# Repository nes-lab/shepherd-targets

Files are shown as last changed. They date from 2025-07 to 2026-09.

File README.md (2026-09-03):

# Target Boards & Firmware





**Main Documentation**: <https://nes-lab.github.io/shepherd>

**Source Code**: <https://github.com/nes-lab/shepherd-targets>

**Main Project**: <https://github.com/nes-lab/shepherd>

---

The repository contains a collection of target-hardware and mcu-firmwares used by the shepherd-testbed.
In the past shepherd had a nRF52-only target but can now leverage an additional FRAM, as demonstrated successfully by the
[Riotee-Platform](https://www.riotee.nessie-circuits.de).

**NOTE**: The shepherd testbed has a second target-port (unused) and is looking for ideas.
Just contact us if you got ideas.

## nRF52 with MSP430FR as FRAM

The current hardware v1.3+ uses

- Nordic nRF52840 - primary MCU with RF
- TI MSP430FR5994 - secondary MCU with low-energy FRAM
- Abracon AB1805 - real-time clock

Target_nRF_MSP430

BOM, gerber-files and schematics are available in the [PCB-Directory](https://github.com/nes-lab/shepherd-targets/tree/main/hardware).
This folder also contains a guide for testing new target-PCBs.

Target_nRF_MSP430_render

### Features

- freedom to use both MCUs as needed (just as radio or FRAM) or disable when not needed (deep sleep)
- over-voltage protection for V_LV (max 3.9V)
- under-voltage protection with hysteresis for nRF
- one debug LEDs with separate supply for minimal impact on pwr-budget
- one self-powered LED to "burn" energy
- io pins not interfering with RF (nRF PS v1.6 page 578)
- LEDs / UART similar to [Riotee](https://www.riotee.nessie-circuits.de/)
- nRF uses low voltage mode (PSv1.1 page 61)
- 16x GPIO shared to host, current-limited with 240R star-configuration (every participant has that resistor on its port to also keep data rates >10 MHz)
- high & low power-good-signal (similar to Riotee)
- SMA-port for external antenna
- RF-Balun optimized for high output power (PS v1.8 ref circuit 7)
- ~~3rd possible way for reset (external)~~, beside jtag and pwr-cycle

### nRF52-Firmwares

- [nrf52_demo_rf](https://github.com/nes-lab/shepherd-targets/tree/main/firmware/nrf52_demo_rf): demo implementation for a simple node that sends BLE packets when energy budget allows it
- [nrf52_testable](https://github.com/nes-lab/shepherd-targets/tree/main/firmware/nrf52_testable): watches all gpio and reports with UART messages (verification after assembly)
  - ensures that pcb is assembled OK and both MCUs are programmable and show basic functions
  - what is not tested: watchdog, FRAM, RF-Frontend (-> use rf-demo or rf-survey), sleep power consumption
- [nrf52_rf_test](https://github.com/nes-lab/shepherd-targets/tree/main/firmware/nrf52_rf_test): sends out 1 BLE-Packet per second (verify with an app like `RaMBLE`)
- [nrf52_rf_survey](https://github.com/nes-lab/shepherd-targets/tree/main/firmware/nrf52_rf_survey): Link Matrix Generator - TX-Unit - sends packet with every possible P_TX, loops until stopped
- [nrf52_deep_sleep](https://github.com/nes-lab/shepherd-targets/tree/main/firmware/nrf52_deep_sleep): practically turned off MCU with the lowest possible consumption
- TODO: nrf52_spi_radio - default implementation to use nRF as a radio frontend

### MSP430FR-Firmwares

- [msp430_deep_sleep](https://github.com/nes-lab/shepherd-targets/tree/main/firmware/msp430_deep_sleep): practically turned off MCU with the lowest possible consumption
- [msp430_spi_fram](https://github.com/nes-lab/shepherd-targets/tree/main/firmware/msp430_spi_fram): [riotee](https://github.com/NessieCircuits/Riotee_MSP430Fram) implementation to use MSP as a flash storage
- [msp430_testable](https://github.com/nes-lab/shepherd-targets/tree/main/firmware/msp430_testable): switches on all shared gpio one by one (verification after assembly)

## Getting started

Step by step description for installing all prerequisites to compile the firmware.

### nRF52

- Make sure you have the [GNU Arm Embedded Toolchain](https://developer.arm.com/tools-and-software/open-source-software/developer-tools/gnu-toolchain/gnu-rm/downloads) installed
- If `arm-none-eabi-gcc` is not in your path, set the environment variable `GNU_INSTALL_ROOT` accordingly
  - e.g. `export GNU_INSTALL_ROOT=/opt/toolchain/` (note the trailing foreslash)
- Download the nRF5 SDK from [here.](https://www.nordicsemi.com/Software-and-tools/Software/nRF5-SDK/Download) (You don't need a SoftDevice) and extract it
- Set the environment variables `SDK_ROOT` to the corresponding absolute path, e.g.: `export SDK_ROOT=/home/user/nRF5_SDK_17.0.2_d674dde/`
- run `make`

Refer to [the GitHub workflow](https://github.com/nes-lab/shepherd-targets/tree/main/.github/workflows/build_nrf.yaml) for how to install the toolchain and build the project.

### MSP430

To build the code, you'll need the gcc toolchain for the MSP430 microcontroller series.
Refer to [the GitHub workflow](https://github.com/nes-lab/shepherd-targets/tree/main/.github/workflows/build_msp.yaml) for how to install the toolchain and build the project.

### Controlling the Node-ID

When an `elf`-firmware contains a ``SHEPHERD_NODE_ID``, the variable will be patched with the actual target-ID before running the experiment.
See the proposed [c-file](https://github.com/nes-lab/shepherd-targets/tree/main/firmware/nrf52_demo_rf/src/shepherd_node_id.c) for more information.

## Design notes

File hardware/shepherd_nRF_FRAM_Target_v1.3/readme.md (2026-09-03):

# nRF52 & MSP430 FRAM Target V1.3

Shared pins between MCUs and Observers with **Cape V2.5 (currently evaluated)**.
**The testbed still uses Cape v2.4 as of 2025-04. See 2nd table below for that mapping.**

| SHP-V26  | Dir   | Riotee     | nRF52  | msp430  | Description                 |
|----------|-------|------------|--------|---------|-----------------------------|
| GPIO0    | <-A-> | GPIO.0     | P0.21  | P2.6    | UART Target-RX, msp.A1.CiPo |
| GPIO1    | <--   | GPIO.1     | P0.08  | P2.5    | UART Target-TX, msp.A1.CoPi |
| GPIO2    | <-B-> | GPIO.2     | P0.04  | P2.3    | msp.A1.PSel                 |
| GPIO3    | <-B-> | GPIO.3     | P0.05  | P2.4    | msp.A1.CLK                  |
| GPIO4    | <-C-> | GPIO.4     | P1.09  | P4.6    |                             |
| GPIO5    | <-C-> | GPIO.5     | P0.26  | P3.6    |                             |
| GPIO6    | <-C-> | GPIO.6     | P1.03  | PJ.6    |                             |
| GPIO7    | <-C-> | GPIO.7     | P0.11  | P5.3    | msp.B1.PSel                 |
| GPIO8    | <--   | GPIO.8     | P0.13  | P5.2    | msp.B1.CLK                  |
| GPIO9    | <--   | GPIO.9     | P0.16  | P5.1    | msp.B1.CiPo                 |
| GPIO10   | <--   | -          | P0.12  | P5.0    | msp.B1.CoPi, SDA            |
| GPIO11   | <--   | -          | P0.10  | P6.0    | msp.A3.CoPi, TXD            |
| (GPIO12) | <--   | -          | P0.19  | P6.1    | msp.A3.CiPo, RXD            |
| (GPIO13) | <--   | -          | P0.20  | P6.3    | msp.A3.STE                  |
| (GPIO14) | <--   | -          | P0.24  | P6.6    | msp.A3.CLK                  |
| (GPIO15) | <--   | -          | P0.27  | P6.7    | msp.A3.STE                  |
| PwrGoodL | -->   | PG_L       | P0.23  | P5.4    |                             |
| PwrGoodH | -->   | PG_H       | P0.07  | P5.5    |                             |
| prog11   | -->   | SWD.CLK    | swdclk | -       |                             |
| prog12   | <-D-> | SWD.IO     | swdio  | -       |                             |
| prog21   | -->   | SBW.CLK    | -      | sbwtck  |                             |
| prog22   | <-E-> | SBW.IO     | -      | sbwtdio |                             |
|          | -     | LED.0      | P1.13  | P5.7    |                             |
|          | -     | LED.2P     | P0.03  | PJ.0    |                             |
|          | -     | I2C.SCL    | P1.08  | P6.5    |                             |
|          | -     | I2C.SDA    | P0.06  | P6.4    |                             |
|          | -     | RTC.INT    | P0.30  | P7.3    | shared, no fct for shp      |
|          | -     | MAX.INT    | P0.25  | PJ.1    | shared, no fct for shp      |
|          | -     | C2C.CLK    | P0.18  | P1.5    | msp.A0.CLK                  |
|          | -     | C2C.CoPi   | P0.17  | P2.0    | msp.A0.CoPi                 |
|          | -     | C2C.CiPo   | P0.14  | P2.1    | msp.A0.CiPo                 |
|          | -     | C2C.PSel   | P0.22  | P1.4    | msp.A0.PSel                 |
|          |       | C2C.GPIO   | P0.15  | PJ.2    |                             |
|          |       | THRCTRL.H0 | P0.09  | P1.3    | shared, no fct for shp      |
|          |       | THRCTRL.H1 | P1.02  | P3.3    | shared, no fct for shp      |
|          |       | THRCTRL.L0 | P1.07  | P6.2    | shared, no fct for shp      |
|          |       | THRCTRL.L1 | P1.04  | P7.0    | shared, no fct for shp      |
|          |       | VCAP.Sense | P0.29  | P7.5    | VTarget                     |

**Note**:

- A, B, C in DIR-Column refer to switch-groups. 1, 2 and/or 4 bits can be reversed to talk to the target.
- D, E are switch-groups needed for programming
- Shepherds GPIO12 to GPIO15 are not recordable by the testbed as pins on the SBC are all used up

## Connections to Cape V2.4 via Adapter

The 40-pin Edge-Connector of Target V1.3 has an adapter to interface the 2x9 Header of Cape V2.4. This keeps connections compatible to Target V1.0.

| SHP-V24 | Dir   | Riotee   | nRF52  | msp430  | Description                 |
|---------|-------|----------|--------|---------|-----------------------------|
| GPIO0   | <-A-> | GPIO.7   | P0.11  | P5.3    | msp.B1.PSel                 |
| GPIO1   | <-A-> | GPIO.8   | P0.13  | P5.2    | msp.B1.CLK                  |
| GPIO2   | <-A-> | GPIO.2   | P0.04  | P2.3    | msp.A1.PSel                 |
| GPIO3   | <-A-> | GPIO.3   | P0.05  | P2.4    | msp.A1.CLK                  |
| GPIO4   | <--   | GPIO.4   | P1.09  | P4.6    |                             |
| GPIO5   | <--   | GPIO.5   | P0.26  | P3.6    |                             |
| GPIO6   | <--   | GPIO.6   | P1.03  | PJ.6    |                             |
| GPIO7   | <--   | GPIO.1   | P0.08  | P2.5    | UART Target-TX, msp.A1.CoPi |
| GPIO8   | <-B-> | GPIO.0   | P0.21  | P2.6    | UART Target-RX, msp.A1.CiPo |
| BATOK   | -->   | PG_H     | P0.07  | P5.5    |                             |
| prog11  | -->   | SWD.CLK  | swdclk | -       |                             |
| prog12  | <-C-> | SWD.IO   | swdio  | -       |                             |
| prog21  | -->   | SBW.CLK  | -      | sbwtck  |                             |
| prog22  | <-D-> | SBW.IO   | -      | sbwtdio |                             |

**Note**:

- A, B, C, D in DIR-Column refer to switch-groups
- Shepherds GPIO8 (target-rx) will be re-assigned to PwrGoodL (BATOK is PwrGoodH)
  - TODO: Resistor-Switch on adapter available, but software not ready yet

## Features

- similarity to Riotee
- MCU 1 - nRF52840
- MCU 2 - msp430FR5994
- low power RTC & Watchdog
- one led to burn energy fast
- SMA port to connect external antenna
  - balun is optimized for higher transmit power (>= 5 dBm, ref circuit 7 in PS v1.8)
- MCUs share SPI-Connection + some additional pins
- edge-connector routes out
  - programming pins (SWD & SBW)
  - power-good signals
  - 16x shared GPIO
- all shared GPIO is current limited to prevent damages to the hardware
  - limit to 8-10 mA @ 4V with 470 R or (2x) 220 R on each IC entry
- IO-Pins not interfering with RF (nRF PS v1.6 page 578)
- clock-crystals have high precision, 5 ppm, with matched impedance
- protection for over- & under-voltage, see sub-chapters below

### Over-Voltage-Protection

The target voltage coming from the shepherd-cape can reach up to 5 V.
The MCUs on the target board can't handle that voltage, so the ICs have to be protected.

Abs Max Ratings:

- 3.9 V nRF52
- 3.8 V RTC AB1805
- 4.1 V MSP430

A fitting shottky diode is used to burn energy above 3.7V.

One PMEG10010ELR Diode is between V_target and 3V3:

- 0.0 V -> 6 pA (noise)
- 0.1 V -> 47 nA
- 0.2 V -> 2.3 uA
- 0.3 V -> 120 uA
- 0.4 V -> 4.83 mA

### Under-Voltage-Protection

- the nRF consumes ~.5mA below 1.7V, even in deep-sleep
- consumption drops when going above 1.69 V
- consumption rises when going below 1.58 V
- tested 13 nodes range from
  - ON = 1.63 to 1.69 V
  - OFF = 1.58 to 1.60 V

Solution

- analog switch controlled by comparator with small hysteresis
- VON = 1.729 V, VOFF = 1.652 V according to formular in datasheet (values are wrong?)
- VON = 1.797 V, VOFF = 1.642 V when solving the network with traditional methods
- VON = 1.802 V, VOFF = 1.641 V from actual measurements

Possible Caveats

- hysteresis is currently only 150 mV and unstable behavior must be avoided
- charging the decoupling caps (2.6 uF) of the MCUs leads to voltage drop
  - 10 uF storage, 2.6 uF decoupling -> 230 mV drop (trouble)
  - 47 uF storage, 2.6 uF decoupling -> 48 mV drop
  - 100 uF storage, 2.6 uF decoupling -> 22 mV drop
- turning on the switch shows current spike of ~ 4 mA for < 50 us for target v1.0 with 1.6 uF decoupling
  - 10 uF storage, 5 mA draw -> 200 us for 100 mV drop
  - 10 uF storage, 1 mA draw -> 1000 us for 100 mV drop
  - 47 uF storage, 5 mA draw -> 940 us for 100 mV drop
  - 100 uF storage, 5 mA draw -> 2000 us for 100 mV drop

Calculating the charging drop for the decoupling caps with `maxima`:

```maxima
C_store: 10e-6;
C_out: 2.6e-6;
V_set: 1.7;
dVc: V_set * (sqrt(1 - C_out / C_store) - 1);
```

Calculating the allowed time for high current during switching on:

```maxima
V_set: 1.7;
C_store: 10e-6;
I_out: 5e-3;
dV: 100e-3;
t: dV * C_store / I_out;
```

See `.wxmx`-maxima-file for more details.

## Difference to Riotee

- nRF52840 instead of Riotees -833
  - main makefile specifies `NRF_DEV_NUM`
- msp430FR5994 has more storage (256 KB)
  - Size of FRAM auto-adjust? -> main makefile `RIOTEE_RAM_RETAINED_SIZE`, `RIOTEE_STACK_SIZE`
- extra LED.0
- 16x GPIO instead of 10x
- no power-converters, but over-voltage-protection and under-volt-switch for nRF

## Bugs of prior Version & Proposed Fixes / Improvements

- nRF - remove resist of alignment crosses
- less paste on thermal pad of nRF? Thermal paste is OK
  - solder on thermal is 9 * 1.1² = 8.6 mm² (round) -> 38 %
  - info: nRF-IC thermal pad ~4.75², 22.6 m² (IC and footprint match)
- make ABx Thermal pad bigger
  - info: ABx-IC thermal pad is ~ (1.8 mm)²
  - datasheet says D2xE2 is 1.65 - 1.75 - 1.85 -> area: 2.6 - 3.1 - 3.4 mm²
  - footprint was (1.13mm)² with 50% paste reduction (1.27 / 0.65 mm²)
  - now it is 1.5² with 65% reduction (2.25 / 0.79 mm²)
- stencil holes of nRF a bit bigger - pad 0.26mm round = 53.1e-3 mm², now with .28mm stencil (.213 distance, 61.6e-3 mm²)
  - ref design: pads .275mm with 19% expansion (.012mm) -> measured .299 (area .0594, .0647, .0702 for .275, .287, .299)
- stencil holes of MSP a bit bigger - pad 0.25mm round = 49.1e-3 mm², now with .28mm stencil (.213 distance)
- 1uF has two versions in BOM -> 10V version stays
- make more clear what is DNP -> Variants "Only Populate" changes Value, Mnf PN, Price to DNP
- Riotee has an MSP430FR5962 (like target v1.0) and not the current 5994?!? (256 vs 128 kByte)
  - linker and makefile needed a small adaption (include proper device-file)
  - Riotees FRAM-firmware is adapting automatically to FRAM-Size
  - datasheets memory map (section 9.15) shows identical maps with just double the FRAM-Space (end at x43FFF instead of x23FFF)
- why did the crystals footprint change (larger) but not the part? tombstone rate ~ 50%
  - correct crystal for that larger footprint: 520-ECX-.327CDX-1293, 5ppm, 3.2x1.5mm -> all correct & available
  - OLD: CM8V-T1A-32.768kHz-9pF-20PPM-TA-QC, 20ppm, 2.0x1.2mm
- add C on ABx-Crystal? YES - datasheet is misleading by not showing any
- board dimensions:
  - capes 54.8 / 2 = 27.4 mm max width -> 27
  - edge-connector, slit-bit is 6 x 17.4 mm -> side cutout is 6 x 4.8
  - target with hdr is 38.2 mm, so limiting the whole length now to 37
  - old-area was 25 x 24 = 600 mm², new usable area is 27 x 31 = 837
- nRF has high current draw between 500...1650 mV -> VSrc with diode+cap is problematic
  - voltage sweep is plotted in [this graphic](emu_ramp.plot_0s000_to_40s000.png) and other
  - add comparator to delay power of nRF
  - fix targets: comparator + pwr-switch -> on when above 1.65 .. 1.70 V
    - off again when going below 1.4 V
  - 2x 6.5 MOhm Divider to
  - ~~TS5A23166DCUR~~ -> needs comparator
  - ~~in our stock: NLAS4684, FSA2258~~
  - 595-TS5A3167DCKR, ROn .9 Ohm, SC70-5, 50nA supply, SPST -> V_analog_max = VCC, V_EN_max = VIn_max = 6.5V
    - COM connected to NC (normally closed) when logic is LOW, so input is nEN!
  - 579-MCP6546RT-IOT, comparator, VIN+ gets Ref ResistorNW, When VIN- is below VIN+ the output is high (WANTED)
    - open drain output, so PU to 3V3 - switch has <20nA leakage, so ~100k should be fine
- extend to 16 GPIO
  - order adapter to old shepherd 2x9
  - order pinheader and sockets for the new port
  - which pins to add?
  - 2x10 Angled Socket: SQT-110-01-F-D-RA -> new 2x13: SQT-113-01-F-D-RA -> without Angle: SQT-113-01-F-D
  - 2x10 PinHeader: 2PH2-20-UA -> new 2x13 only available from samtec, but they fit next to each other -> 2PH2-16-UA + 2PH2-10-UA
  - width: 20.35/10*13=26.5mm or better 20.35/11*14=25.9mm, MAX of Cape is 54.7/2=27.35mm
  - PCB-Edge-Connectors: <https://www.mouser.de/c/connectors/card-edge-connectors/?number%20of%20positions=26%20Position%7C~30%20Position&instock=y&active=y&sort=pricing>
    - PCIe 1x is cheap, has 1 mm distance and comes as TH & SMD, but it is designed for thick PCBs
    - HSEC8-120-01-S-DV-A-GR-K: 40Con, Guide Rails 7x20.6mm 11.75mm high
    - HSEC8-120-01-S-DV-A-K: without guide rails only 7.8mm high
    - **HSEC8-120-01-L-DV-A-K-TR**: same, but cheaper
  - ~~FFC/FPC-Con~~: <https://www.mouser.de/c/connectors/ffc-fpc/ffc-fpc-connectors/?number%20of%20positions=26%20Position%7C~28%20Position%7C~30%20Position%7C~32%20Position&instock=y&active=y>
  - ~~FFC/FPC-Cable~~: <https://www.mouser.de/c/connectors/ffc-fpc/ffc-fpc-jumper-cables/?number%20of%20conductors=26%20Conductor%7C~28%20Conductor%7C~30%20Conductor%7C~32%20Conductor&instock=y&active=y>
- current-limit LED0 (MSP430 is lower prio, so it gets 470R)
- **NEW GPIO**
  - GP10 P0.12  P5.0 (UCB1SIMO/SDA)
  - GP11 P0.10  P6.0 (UCA3SIMO/TXD)
  - GP12 P0.19  P6.1 (UCA3SOMI/RXD)
  - GP13 P0.20  P6.3 (UCA3STE)
  - GP14 P0.24  P6.6 (UCA3CLK)
  - GP15 P0.27  P6.7 (UCA3STE)
  - LED0 P1.13  P5.7
- verify RF-Path
  - PS_v1.8 ref circuit 7 shows improved 4 component filter: 1pF, 4.7nH, 1.2pF, 2.2nH (NP0 5%, hf ind. 5%)
  - keepout under antenna-path for
  - fanout shorter and thinner, C1 directly on RFOUT and GND
- review problematic pins
- also disable MSP with switch (avoids cross-feeding via gpio)

## Cost of Production

- PCB-Fabrication
  - 190 € / 30 n with shipping
  - 1.6mm thick, 4 layer, .3mm vias - filled and capped, .1 mm traces and distance
  - electro-polished stencil
- BOM cost
  - parts for 1 n when ordering 10 n = 20.60 €
  - parts for n=10 are 182 € (18.20 €/n)
  - parts for n=20 are 360 € (18 €/n)
- Pick & place
  - 29 different parts, 120 in total
  - 0.5 mm pitch

### Ordering of Parts

- new C27 1pF: 100x 81-GJM1555C1H1R0JB1D
- new C28 1.2pF: 100x 81-GJM1555C1H1R2JB1D
- new L2 2.2nH: 100x 81-LQG15HZ2N2C02D
- ~~SMA-Con?~~
- new HSEC8-120-01-L-DV-A-K-TR: 20x 200-HSEC812001LDVAKT
  - new headers for old cape?
- more 1uF - 4x30 - 200x 81-GCM155C71A105KE8D
- more 12pF -8x30 - 250x 77-VJ0402A120JXQPBC
- 12x 240R per unit (more IO)
- switch + comparator (MCP6546, TS5A3167)
  - 3x 100k, 1x 10k, 1x 1M,
  - 2x 100nF
- 1x 470R

### Extra remark

- DNP: C20, SMA-Con, Antenna

## Verifying the PCBs

- first do a visual inspection
- front side has one cap DNP: C20, lower left corner, near edge-connector

### Assembly

- solder the SMA-Connector, add Antenna

### First Powerup

- 2 mA @ 3V on V_target without programming
- 0 mA @ 3V on 3V-Input

### Software-Prereqs

**NOTE**: all further tests are done on BBone

```Shell
cd ~
git clone https://github.com/nes-lab/shepherd-tools
cd shepherd-tools
git checkout dev
git pull

python3 ./extra/gen_firmwares.py
sudo python3 ./extra/gen_experiments.py
```

Put Target on BBone with Target on Port 1!

### Test all GPIO & LEDs

First test all used gpio with this fw-combo (msp toggles, nrf watches and reports via uart):

```Shell
sudo shepherd-sheep program -p A -m 1 -v 3 -t nrf52 /var/shepherd/content/fw/nes_lab/nrf52_testable/build.hex
sudo shepherd-sheep program -p A -m 2 -v 3 -t msp430 /var/shepherd/content/fw/nes_lab/msp430_testable/build.hex
sudo shepherd-sheep target-power -p A -v 3 --on
# new
sudo shepherd-sheep run /etc/shepherd/target_device_test1.yaml
```

NOTE: best done with inter-connector that only routes: pwr1, serial, programming-pins, pwr2
Check UART output with logic analyzer or in shepherd recording.
Behavior is described in [the firmware-directory](https://github.com/nes-lab/shepherd-targets/tree/main/firmware/nrf52_testable).

### Testing the Radio

```Shell
sudo shepherd-sheep program -p A -m 1 -v 3 -t nrf52 /var/shepherd/content/fw/nes_lab/nrf52_rf_test/build.hex
sudo shepherd-sheep program -p A -m 2 -v 3 -t msp430 /var/shepherd/content/fw/nes_lab/msp430_deep_sleep/build.hex
sudo shepherd-sheep target-power -p A -v 3 --on
# new
sudo shepherd-sheep run /etc/shepherd/target_device_test2.yaml
```

Behavior is described in [the firmware-directory](https://github.com/nes-lab/shepherd-targets/tree/main/firmware/nrf52_rf_test).

### Testing Power-consumption during sleep

```Shell
sudo shepherd-sheep program -p A -m 1 -v 3 -t nrf52 /var/shepherd/content/fw/nes_lab/nrf52_deep_sleep/build.hex
sudo shepherd-sheep program -p A -m 2 -v 3 -t msp430 /var/shepherd/content/fw/nes_lab/msp430_deep_sleep/build.hex
# new
sudo shepherd-sheep run /etc/shepherd/target_device_test3.yaml
```

## Testing

- programming via debug-adapter fails for nRF (OK for MSP), even at 200kbit or 100kbit instead of 500k
  - reason: unsoldered press-fit to shepherd cape
- 6 of 24 targets had trouble programming the MSP
  - removing two ICs showed no flaws
  - as visual inspection is OK the next suspects are: pcb or chip-failure
- report is in [planning-repo](https://github.com/orgua/shepherd-v2-planning/tree/main/doc_testbed)

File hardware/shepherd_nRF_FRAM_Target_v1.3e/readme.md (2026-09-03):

# nRF52 & MSP430 FRAM Target V1.3e

Shared pins between MCUs and Observers with **Cape V2.5 (deployed in near future / mid 2025)**.

~~The testbed still uses Cape v2.4 as of 2025-04. See 2nd table below for that mapping.~~

**Note**:

- GPIO12 to GPIO15 are not recordable by the testbed with cape V2.5, as pins on the SBC are all used up
- The nRF has no outer reset line
  - configuring one could keep the MCU in permanent reset
  - Code for the nRF52-DK may use P0.21 for reset - it is actively used for UART-Rx here.
- A, B, C in DIR-Column refer to switch-groups. 1, 2 and/or 4 bits can be reversed to talk to the target.
- D, E are switch-groups needed for programming

| Tgt-Port | Dir   | Riotee     | nRF52  | msp430  | Description                 |
|----------|-------|------------|--------|---------|-----------------------------|
| GPIO0    | <-A-> | GPIO.0     | P0.21  | P2.6    | UART Target-RX, msp.A1.CiPo |
| GPIO1    | <--   | GPIO.1     | P0.08  | P2.5    | UART Target-TX, msp.A1.CoPi |
| GPIO2    | <-B-> | GPIO.2     | P0.04  | P2.3    | msp.A1.PSel                 |
| GPIO3    | <-B-> | GPIO.3     | P0.05  | P2.4    | msp.A1.CLK                  |
| GPIO4    | <-C-> | GPIO.4     | P1.09  | P4.6    |                             |
| GPIO5    | <-C-> | GPIO.5     | P0.26  | P3.6    |                             |
| GPIO6    | <-C-> | GPIO.6     | P1.03  | PJ.6    |                             |
| GPIO7    | <-C-> | GPIO.7     | P0.11  | P5.3    | msp.B1.PSel                 |
| GPIO8    | <--   | GPIO.8     | P0.13  | P5.2    | msp.B1.CLK                  |
| GPIO9    | <--   | GPIO.9     | P0.16  | P5.1    | msp.B1.CiPo                 |
| GPIO10   | <--   | -          | P0.12  | P5.0    | msp.B1.CoPi, SDA            |
| GPIO11   | <--   | -          | P0.10  | P6.0    | msp.A3.CoPi, TXD            |
| (GPIO12) | <--   | -          | P0.19  | P6.1    | msp.A3.CiPo, RXD            |
| (GPIO13) | <--   | -          | P0.20  | P6.3    | msp.A3.STE                  |
| (GPIO14) | <--   | -          | P0.24  | P6.6    | msp.A3.CLK                  |
| (GPIO15) | <--   | -          | P0.27  | P6.7    | msp.A3.STE                  |
| PwrGoodL | -->   | PG_L       | P0.23  | P5.4    |                             |
| PwrGoodH | -->   | PG_H       | P0.07  | P5.5    |                             |
| prog11   | -->   | SWD.CLK    | swdclk | -       |                             |
| prog12   | <-D-> | SWD.IO     | swdio  | -       |                             |
| prog21   | -->   | SBW.CLK    | -      | sbwtck  |                             |
| prog22   | <-E-> | SBW.IO     | -      | sbwtdio |                             |
|          | -     | LED.0      | P1.13  | P5.7    |                             |
|          | -     | LED.2P     | P0.03  | PJ.0    |                             |
|          | -     | I2C.SCL    | P1.08  | P6.5    |                             |
|          | -     | I2C.SDA    | P0.06  | P6.4    |                             |
|          | -     | RTC.INT    | P0.30  | P7.3    | shared, no fct for shp      |
|          | -     | MAX.INT    | P0.25  | PJ.1    | shared, no fct for shp      |
|          | -     | C2C.CLK    | P0.18  | P1.5    | msp.A0.CLK                  |
|          | -     | C2C.CoPi   | P0.17  | P2.0    | msp.A0.CoPi                 |
|          | -     | C2C.CiPo   | P0.14  | P2.1    | msp.A0.CiPo                 |
|          | -     | C2C.PSel   | P0.22  | P1.4    | msp.A0.PSel                 |
|          |       | C2C.GPIO   | P0.15  | PJ.2    |                             |
|          |       | THRCTRL.H0 | P0.09  | P1.3    | shared, no fct for shp      |
|          |       | THRCTRL.H1 | P1.02  | P3.3    | shared, no fct for shp      |
|          |       | THRCTRL.L0 | P1.07  | P6.2    | shared, no fct for shp      |
|          |       | THRCTRL.L1 | P1.04  | P7.0    | shared, no fct for shp      |
|          |       | VCAP.Sense | P0.29  | P7.5    | VTarget                     |

## Connections to Cape V2.4 via Adapter

The 40-pin Edge-Connector of Target V1.3 has an adapter to interface the 2x9 Header of Cape V2.4.
This keeps connections compatible to Target V1.0.

**Note**:

- A, B, C, D in DIR-Column refer to switch-groups
- Shepherds GPIO8 (target-rx) will be re-assigned to PwrGoodL (BATOK is PwrGoodH)

| SHP-V24 | Dir   | Riotee   | nRF52  | msp430  | Description                 |
|---------|-------|----------|--------|---------|-----------------------------|
| GPIO0   | <-A-> | GPIO.7   | P0.11  | P5.3    | msp.B1.PSel                 |
| GPIO1   | <-A-> | GPIO.8   | P0.13  | P5.2    | msp.B1.CLK                  |
| GPIO2   | <-A-> | GPIO.2   | P0.04  | P2.3    | msp.A1.PSel                 |
| GPIO3   | <-A-> | GPIO.3   | P0.05  | P2.4    | msp.A1.CLK                  |
| GPIO4   | <--   | GPIO.4   | P1.09  | P4.6    |                             |
| GPIO5   | <--   | GPIO.5   | P0.26  | P3.6    |                             |
| GPIO6   | <--   | GPIO.6   | P1.03  | PJ.6    |                             |
| GPIO7   | <--   | GPIO.1   | P0.08  | P2.5    | UART Target-TX, msp.A1.CoPi |
| GPIO8   | <-B-> | GPIO.0   | P0.21  | P2.6    | UART Target-RX, msp.A1.CiPo |
| BATOK   | -->   | PG_H     | P0.07  | P5.5    |                             |
| prog11  | -->   | SWD.CLK  | swdclk | -       |                             |
| prog12  | <-C-> | SWD.IO   | swdio  | -       |                             |
| prog21  | -->   | SBW.CLK  | -      | sbwtck  |                             |
| prog22  | <-D-> | SBW.IO   | -      | sbwtdio |                             |

## Features

- similarity to Riotee
- MCU 1 - nRF52840
- MCU 2 - msp430FR5994
- low power RTC & Watchdog
- one led to burn energy fast
- SMA port to connect external antenna
  - balun is optimized for higher transmit power (>= 5 dBm, ref circuit 7 in PS v1.8)
- MCUs share SPI-Connection + some additional pins
- edge-connector routes out
  - programming pins (SWD & SBW)
  - power-good signals
  - 16x shared GPIO
- all shared GPIO is current limited to prevent damages to the hardware
  - limit to 8-10 mA @ 4V with 470 R or (2x) 220 R on each IC entry
- IO-Pins not interfering with RF (nRF PS v1.6 page 578)
- clock-crystals have high precision, 5 ppm, with matched impedance
- protection for over- & under-voltage, see sub-sections below

### Over-Voltage-Protection

The target voltage coming from the shepherd-cape can reach up to 5 V.
The MCUs on the target board can't handle that voltage, so the ICs have to be protected.

Abs Max Ratings:

- 3.9 V nRF52
- 3.8 V RTC AB1805
- 4.1 V MSP430

A fitting shottky diode is used to burn energy above 3.7V.

One PMEG10010ELR Diode is between V_target and 3V3:

- 0.0 V -> 6 pA (noise)
- 0.1 V -> 47 nA
- 0.2 V -> 2.3 uA
- 0.3 V -> 120 uA
- 0.4 V -> 4.83 mA

### Under-Voltage-Protection

- the nRF consumes ~.5mA below 1.7V, even in deep-sleep
- consumption drops when going above 1.69 V
- consumption rises when going below 1.58 V
- tested 13 nodes range from
  - ON = 1.63 to 1.69 V
  - OFF = 1.58 to 1.60 V

Solution

- analog switch controlled by comparator with small hysteresis
- VON = 1.729 V, VOFF = 1.652 V according to formular in datasheet (values are wrong?)
- VON = 1.797 V, VOFF = 1.642 V when solving the network with traditional methods
- VON = 1.802 V, VOFF = 1.641 V from actual measurements

Possible Caveats

- hysteresis is currently only 150 mV and unstable behavior must be avoided
- charging the decoupling caps (2.6 uF) of the MCUs leads to voltage drop
  - 10 uF storage, 2.6 uF decoupling -> 230 mV drop (trouble)
  - 47 uF storage, 2.6 uF decoupling -> 48 mV drop
  - 100 uF storage, 2.6 uF decoupling -> 22 mV drop
- turning on the switch shows current spike of ~ 4 mA for < 50 us for target v1.0 with 1.6 uF decoupling
  - 10 uF storage, 5 mA draw -> 200 us for 100 mV drop
  - 10 uF storage, 1 mA draw -> 1000 us for 100 mV drop
  - 47 uF storage, 5 mA draw -> 940 us for 100 mV drop
  - 100 uF storage, 5 mA draw -> 2000 us for 100 mV drop

Calculating the charging drop for the decoupling caps with `maxima`:

```maxima
C_store: 10e-6;
C_out: 2.6e-6;
V_set: 1.7;
dVc: V_set * (sqrt(1 - C_out / C_store) - 1);
```

Calculating the allowed time for high current during switching on:

```maxima
V_set: 1.7;
C_store: 10e-6;
I_out: 5e-3;
dV: 100e-3;
t: dV * C_store / I_out;
```

See `.wxmx`-maxima-file for more details.

## Difference to Riotee

- nRF52840 instead of Riotees -833
  - main makefile specifies `NRF_DEV_NUM`
- msp430FR5994 has more storage (256 KB)
  - Size of FRAM auto-adjust? -> main makefile `RIOTEE_RAM_RETAINED_SIZE`, `RIOTEE_STACK_SIZE`
- extra LED.0
- 16x GPIO instead of 10x
- no power-converters, but over-voltage-protection and under-volt-switch for nRF
- no way to sample capacitor voltage (only if vsource is configured without buck-converter, so v_target ~= v_storage)

## Cost of Production

- PCB-Fabrication
  - 190 € / 30 n with shipping
  - 1.6mm thick, 4 layer, .3mm vias - filled and capped, .1 mm traces and distance
  - electro-polished stencil
- BOM cost
  - parts for 1 n when ordering 10 n = 20.60 €
  - parts for n=10 are 182 € (18.20 €/n)
  - parts for n=20 are 360 € (18 €/n)
- Pick & place
  - 29 different parts, 120 in total
  - 0.5 mm pitch

### Extra remark

- DNP: C20, SMA-Con, Antenna

## Verifying the PCBs

- first do a visual inspection
- front side has one cap DNP: C20, lower left corner, near edge-connector

### Assembly

- solder the SMA-Connector, add Antenna

### First Powerup

- 2 mA @ 3V on V_target without programming
- 0 mA @ 3V on 3V-Input

### Software-Prereqs

**NOTE**: all further tests are done on BBone

```Shell
cd ~
git clone https://github.com/nes-lab/shepherd-tools
cd shepherd-tools
git checkout dev
git pull

python3 ./extra/gen_firmwares.py
sudo python3 ./extra/gen_experiments.py
```

Put Target on BBone with Target on Port 1!

### Test all GPIO & LEDs

First test all used gpio with this fw-combo (msp toggles, nrf watches and reports via uart):

```Shell
sudo shepherd-sheep program -p A -m 1 -v 3 -t nrf52 /var/shepherd/content/fw/nes_lab/nrf52_testable/build.hex
sudo shepherd-sheep program -p A -m 2 -v 3 -t msp430 /var/shepherd/content/fw/nes_lab/msp430_testable/build.hex
sudo shepherd-sheep target-power -p A -v 3 --on
# new
sudo shepherd-sheep run /etc/shepherd/target_device_test1.yaml
```

NOTE: best done with inter-connector that only routes: pwr1, serial, programming-pins, pwr2
Check UART output with logic analyzer or in shepherd recording.
Behavior is described in [the firmware-directory](https://github.com/nes-lab/shepherd-targets/tree/main/firmware/nrf52_testable).

### Testing the Radio

```Shell
sudo shepherd-sheep program -p A -m 1 -v 3 -t nrf52 /var/shepherd/content/fw/nes_lab/nrf52_rf_test/build.hex
sudo shepherd-sheep program -p A -m 2 -v 3 -t msp430 /var/shepherd/content/fw/nes_lab/msp430_deep_sleep/build.hex
sudo shepherd-sheep target-power -p A -v 3 --on
# new
sudo shepherd-sheep run /etc/shepherd/target_device_test2.yaml
```

Behavior is described in [the firmware-directory](https://github.com/nes-lab/shepherd-targets/tree/main/firmware/nrf52_rf_test).

### Testing Power-consumption during sleep

```Shell
sudo shepherd-sheep program -p A -m 1 -v 3 -t nrf52 /var/shepherd/content/fw/nes_lab/nrf52_deep_sleep/build.hex
sudo shepherd-sheep program -p A -m 2 -v 3 -t msp430 /var/shepherd/content/fw/nes_lab/msp430_deep_sleep/build.hex
# new
sudo shepherd-sheep run /etc/shepherd/target_device_test3.yaml
```

## Testing

- programming via debug-adapter fails for nRF (OK for MSP), even at 200kbit or 100kbit instead of 500k
  - reason: unsoldered press-fit to shepherd cape
- 6 of 24 targets had trouble programming the MSP
  - removing two ICs showed no flaws
  - as visual inspection is OK the next suspects are: pcb or chip-failure
- report is in [planning-repo](https://github.com/orgua/shepherd-v2-planning/tree/main/doc_testbed)

## Implemented Changes / Bugs of prior Version

- Edge-Connector is 17.40 mm wide, PCB-Edge has 17.20 mm, exactly to spec
  - resist bridge between pads is 0.3 mm, so this is fine, but pcb can be moved
  - -> still widen edge on both sides .05 mm to 17.30 mm (measures as 17.25 mm on final PCB)
  - connector wiggles and prongs are almost on outer edge of pad
- edge-connector is still a bit loose,
  - PCB has only 1.48 mm thickness without copper, resist, silk, but outer rail of connector is 1.75 mm (spec)
  - 1.64 to 1.70 mm on Cu, silk, resist -> measures as 1.64
  - railing edge now has resist and silk screen
- as 6 of 24 MSP430s were failing to be programmed - programming pins were checked & redone
  - R61 is 47k, but measures 4.0k? on failing boards R<3.9k, on good ones larger, more like 4.1
  - optimize via-placement with regard to distance from pad
- update parts from Libs
- panel - move holes of bridges a bit further out
- finished as v1.3e

## Production of v1.3e

- BOM for 30n with spare, 650 € @ Mouser
- Panels for 30n, 214 € @ JLCPCB

## Errata & future Improvements

- add reset line(s) to better handle soft-bricked MCUs
  - needs 1-2x additional GPIO from Host (2 available) and Pins on target connector
  - nRST of both MCUs could be combined to 1 Pin
  - nRST is often default, could be negated on new target PCBs if needed
  - current 40 Pin target-connector has two NC pins left
- allow [using internal switching regulator from nRF to lower power-consumption](https://github.com/nes-lab/shepherd-targets/issues/42)
  - current firmware is forward-compatible (but newer not backward-compat)
  - add L 10uH & 15nH from DCC to DEC4 (1V3) and 1uF & 47nF to GND
  - ~~HV add L 10uH from DCCH to VDD, remove connection between VDDH to VDD~~
  - DK uses both, but MSP, RTC & NRF-VL limit voltage to max 3.8 V
  - contra HV: current design directly connects HV- & LV-input
- allow routing AUX-voltage (second output of DAC) to the same target port
  - mimic V_Sense to allow developing better intermittent algorithms (allows sensing emulated V_harvest or V_storage_cap)
  - needs one additional pin on target connector -> current 40 Pin target-connector has two NC pins left
  - Needs one additional GPIO from Host -> two GPIO available for the analog switch (48, 117) - can be slow sysgpio
- remove Copper below edge connector (if it stays)
  - the connector should get a chamfer (as it breaks the expensive connector)
  - alternative: switch to FPC or FFC, as it is cheaper
- replace edge-connector with flex connector? (FPC or FCC / FFC)
  - contra: current setup is rigid and easy to transport without a case
  - pro: freely position targets in case
  - pro: automatically rotation-safe
  - pro: more usable GPIO on same 40x-Connector (needs less additional GND-Shielding)
  - pro: easier to replace, cheaper,
  - features to keep: rotation-safe & shielded (currently 12x extra GND)
  - needed IO: 16 GPIO, 2 Voltages, 2 PwrGood, 4 Prog, 1+ GND => 25+ Pins
    - +1x for aux voltage
    - +1x for reset line (nRF & msp have nReset) -> 2 lines or negate if needed
    - +2x-3x for I2C-EEPROM (Write-Protection)
    - in total 5 pins extra
  - 40 pin FFC/FPC, 0.5 mm Pitch, 1.5€ -> 05-40-A-0050-A-4-06-4-T-HF
  - 40 pin connector has similar space req. as edge connector, 0.5 € per connector, FFC2B35-40-G
- add small eeprom? allows identifying targets in testbed (device inventory can query itself)
  - optional - when programmers are capable to read the UID of the MCUs (OpenOCD now can)
  - needs 3 additional pins on target-port
- BGA without paste? MSP-failure-rate stays ~ 20 %
  - low temp paste is harder to control - does not wet as good and needs manual fixes (almost on every PCB)
- bridge to panel should be moved away from BGA
- holes on panel can be 3.2 mm for stencil printer
- QR Code can now be directly created in Altium
- perforated breaking lines on panels (extension of milled line)
- bridge to panel can be thinner
- move LED away from SMA
- pin 1 marking bigger on ICs
- is there a paste-pad under the TS5A?

TODO:

- test connecting resets

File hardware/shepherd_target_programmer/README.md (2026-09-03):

# Shepherd Target Programmer

This device allows powering Target-PCBs and programming both MCUs.
It is based on the [Riotee-probe](https://www.riotee.nessie-circuits.de/docs/latest/hardware/probe.html).

This directory contains:

- schematics,
- designfiles,
- BOM and
- assembly drawings

## Supply Firmware

First the Firmware [probe_riotee_board_xyz.hex](https://github.com/NessieCircuits/Riotee_ProbeSoftware/releases) has to be flashed to the RP2040.
Simply hold the `Bootsel`-Button while connecting the board to your PC.
A flash-drive should appear were you can pull in the .hex-file.
The window closes and the firmware gets flashed.

## Install ProbeSoftware

To use the programmer, the Riotee platform provides a probe-software.
You can install it via your preferred python package-manager.
Here pip is used:

```Shell
pip install riotee-probe
```

For more up to date features you can also directly install from git:

```Shell
pip install git+https://github.com/NessieCircuits/Riotee_ProbeSoftware@main#subdirectory=tool
```

## Programming Targets

Some [demo-firmwares are available in the release-section](https://github.com/nes-lab/shepherd-targets/releases) of this repo.

The programmer can be used like that:

```Shell
riotee-probe program -d msp430 -f ./msp430_deep_sleep/build.hex
riotee-probe program -d nrf52 -f ./nrf52_deep_sleep/build.hex

riotee-probe program -d msp430 -f ./msp430_testable/build.hex
riotee-probe program -d nrf52 -f ./nrf52_testable/build.hex

riotee-probe program -d nrf52 -f ./nrf52_rf_test/build.hex
# sends 1 BLE packet per second, Shepherd-beacon, MAC 00:01:02:03:04:05
```

If the nRF52 fails to program with an error similar to

```text
  File "C:\Users\hans\AppData\Local\Programs\Python\Python313\Lib\site-packages\pyocd\probe\cmsis_dap_probe.py", line 684, in write_ap_multiple
    raise self._convert_exception(exc) from exc
pyocd.core.exceptions.TransferFaultError: Memory transfer fault @ 0x20004000-0x200040c3
```

the underlying PyOCD can be used to perform a chip-erase:

```Shell
pyocd erase --mass -v -f 1000 -t nrf52840
pyocd erase --chip -v -f 1000 -t nrf52840
# + powercycle
# NOTE: one of the two commands should suffice
```

## Interfacing Targets

The target-connector only routes the programming lines and UART (Shepherd GPIO 0 & 1).
See [gpio-table here](https://github.com/nes-lab/shepherd-targets/tree/main/hardware/shepherd_nRF_FRAM_Target_v1.3e#nrf52--msp430-fram-target-v13e).

Note that the programmer does not cut power to the target like the Riotee probe does.
Some operations need a power-cycle - for that you could replug the USB-Connector.

To capture all GPIO a logic analyzer and [debug adapter](https://github.com/nes-lab/shepherd-targets/tree/main/hardware/adapter_target_v1.3_debug_big) need to be used.

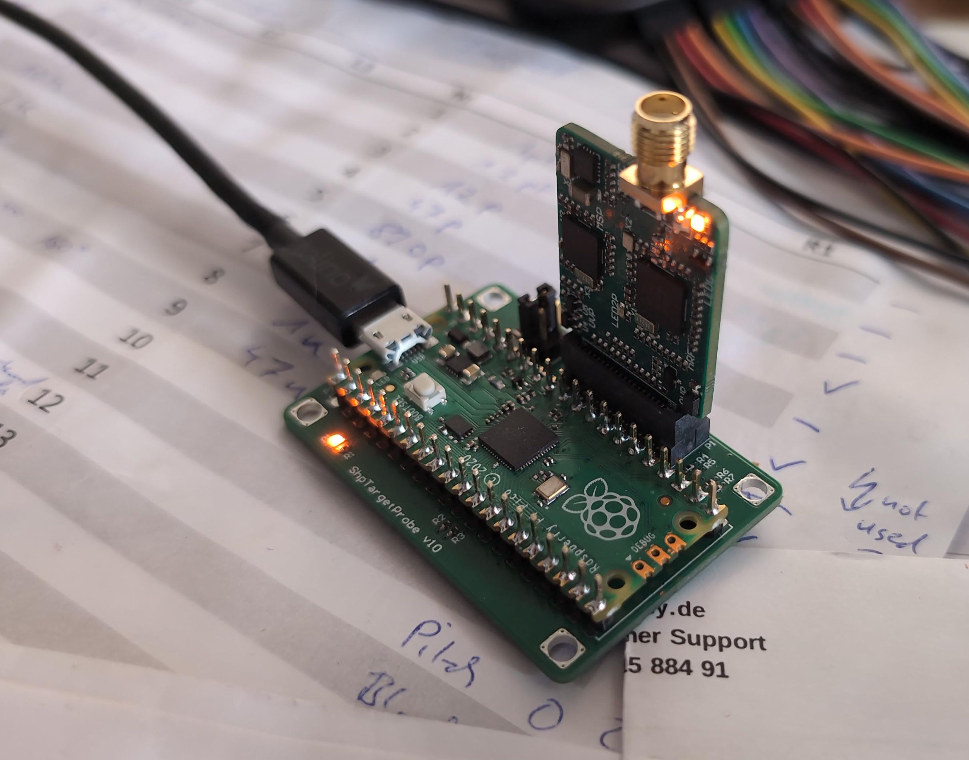
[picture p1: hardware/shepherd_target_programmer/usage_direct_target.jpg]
usage_direct


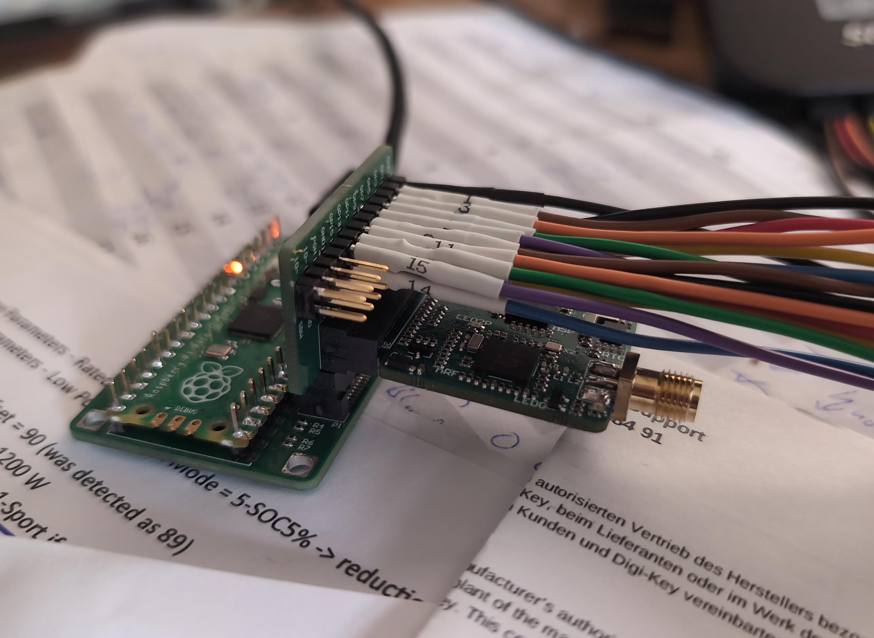
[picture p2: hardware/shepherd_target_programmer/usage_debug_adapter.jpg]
usage_adapter


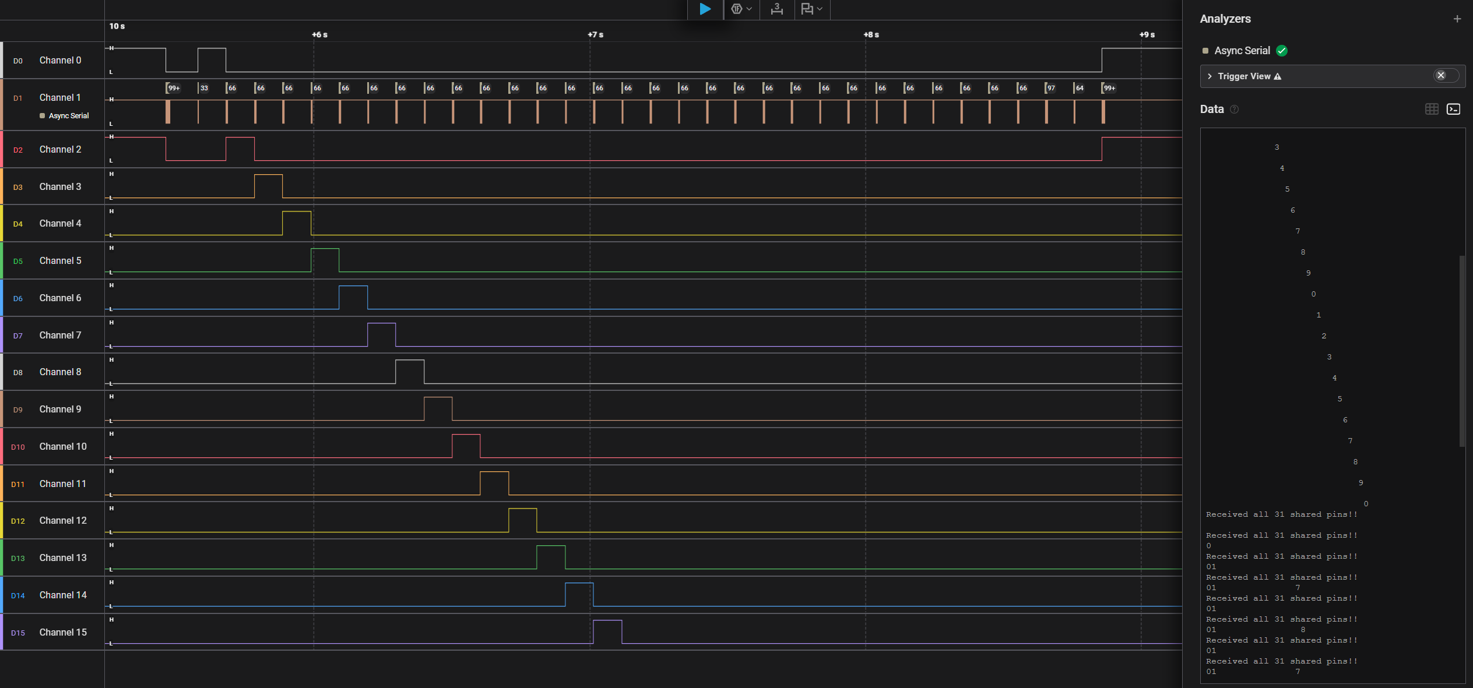
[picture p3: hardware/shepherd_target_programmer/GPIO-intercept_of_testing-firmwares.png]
testing-firmwares


## References

- [test-report of targets - first batch](https://github.com/orgua/shepherd-v2-planning/blob/main/doc_testbed/Target_v13_pre-deployment-tests.xlsx)
- [test-report of targets - 2025 batch](https://github.com/orgua/shepherd-v2-planning/blob/main/doc_testbed/Target_v13e_pre-deployment-tests.xlsx)

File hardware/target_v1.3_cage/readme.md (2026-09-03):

# Cage for Target

This is a printable cage that protect the sensitive electronics.
Biofilm could add a resistive layer on the PCB that increases power-consumption of the target.

Printing was tested top-down with PLA. Support for the overhang can be added, but it also worked fine without it.

cagedTarget

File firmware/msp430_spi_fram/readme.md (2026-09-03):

# MSP430 as SPI-FRAM (non-volatile memory)

The code in this repository turns an MSP430FR59XX microcontrollers into a general purpose non-volatile memory controlled via SPI.

The MSP430FR59XX series of microcontrollers come with on-board ferroelectric RAM (FRAM).
In contrast to SRAM, this memory is non-volatile, i.e. it keeps its state without requiring periodic refreshes and without requiring a power supply.
In contrast to flash memory, which must be erased before being written, FRAM can be treated just like SRAM and writing consumes very little energy.

NOTE: Makefile & linker are currently configured for the MSP430FR5994 (256 KB FRAM) instead of Riotees original FR5962 (128 KB)

## Interface

The firmware in this repository exposes a 4-wire SPI interface that allows reading and writing data to the on-board FRAM.
The SPI interface uses mode 0 (Clock low when inactive, data sampled on leading edge) and supports a frequency of 8MHz.

After the SPI controller pulls the CS line low, the peripheral (this firmware) sets up an initial transfer of 3 control bytes.
These three control bytes contain the 20-bit target address of the memory access and the type of operation (R/W).
The address is transferred lowest byte first.
If the highest bit of the third address byte is set, the operation is a write operation, otherwise it is a read operation.
After receiving the three command bytes, the peripheral will set up the corresponding DMA transfer and wait in a low power mode until the CS line goes high.
The controller shall keep the CS line low until the transfer has finished.
Upon this rising edge, the peripheral stops the transfer and transitions to low power mode again.

Transfers can have a maximum size of 65535 bytes.

## Timing requirements

The time from the falling edge of the CS line until the transmission of the first command byte must be at least 15us.
The time from the transmission of the last command byte to the transmission of the first data byte must be at least 25us.
The time from the rising edge of the CS line until the next falling edge of the CS line must be at least 10us.

## Memory map

The MSP430FR5962 has a total of 128kB FRAM.
Unfortunately, the interrupt vector table lives in the middle of this memory so the 128kB cannot be used contiguously. Instead, they are separated into two regions.
The lower region starts at 0x4000 and ends at 0xFF80 where the IVT lives.
The upper region starts at 0xFFFF and ends at 0x24000.
The code/data for this firmware also has to be placed within this area.
The linker script in this repository defines a dedicated section for the code and data of the firmware ranging from 0x4000 to 0x6000.

The remaining memory area from 0x6000 to 0x24000, excluding the IVT (0xFF80-0xFFFF) is available as data storage.
For an external application talking to the device over SPI, this memory gets mapped to 0x0000 to 0x1E000.
The firmware will protect the IVT from access.
Any operation extending over the IVT region or the end of the memory will get truncated without the controller noticing.

**The code on the SPI controller talking to this firmware must avoid reading/writing to the IVT region, which lies between 0x9F80 and 0x9FFF from its view.**

## Source

<https://github.com/NessieCircuits/Riotee_MSP430Fram>

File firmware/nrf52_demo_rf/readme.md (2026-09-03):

# nrf52 demo for harvesting and rf

This firmware represents a typical intermittent application on a battery-free sensor node.
The app monitors the supply voltage and a GPIO pin.
It sends a BLE advertisement packet and switches on an LED If the supply voltage reaches 3.3 V or the pin goes high.
The LED stays on until the supply voltage drops below 3.3 V or the pin goes low.
The supply voltage is sampled with a frequency of 100 Hz.
The total current consumption in this mode is 5.6 uA.

Edit the definitions of the GPIO pins at the top of `src/app.c` to reflect your hardware.

An App like `LightBlue` or `RaMBLE` can be used to monitor rf-activity.

## Source

<https://github.com/geissdoerfer/shepherd-nrf52-demo>

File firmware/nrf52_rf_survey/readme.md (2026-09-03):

# nRF using TrafficBench to survey the rf-conditions for the testbed

Trafficbench is configured to let each node send a packet. The other nodes listen automatically and try to capture the packet and also record the P_Rx.

Current configuration

- loop - one node after the other talks - the others listen
- each node sends ~ 34 bytes via 1 MBit Bluetooth (~300 us airtime), PTx = 0 dBm
- the other nodes listen and capture for 5 ms (+ 500 us pre- & post-delay)
- sleep 1 s before next node begins

## Installation

- adapt schedule with the [schedule-builder-script](schedule_builder/build.py)
- compiling: follow the [readme](trafficbench/README.md) of trafficbench
  - newest studio version (tested with v7.30) is fine
  - extra package needed (and restart studio after install) - should be automatic: CMSIS 5 5 CMSIS-CORE Support Package

## Usage of ELF

- patch SHEPHERD_NODE_ID in elf-file for each node (see [example python script](./_build/update_and_patch.py))
- run on testbed
- postprocessing, TODO
- NOTE: first loop-cycle should be discarded

## Changes compared to vanilla trafficbench

- change testbed: flocklab -> shepherd
- correct spelling
- fix formatting
- fix for sensitivity to include-order: added #include "traffic_bench.h" in cbor.h
- removed node-id-magic in main.c (line 154:217)
- transformed py-scripts to be more accessible

specially for shepherd

- reduced uart-speed to 115_200 for now (in config.h)
- disable flow control (readme warns about it) to just stream uart (`mode=0` in config.h)
- disable button press to start (section removed in main.c)
- deactivate DEBUG_GPIO in `radio.c`
- current GPI modifications
  - reformatted with projects clang-format
  - use `GPI_ARCH_BOARD_TUDNES_SHEPHERD_NRF52840FRAM_V13` as `GPI_ARCH_PLATFORM` in `trafficbench/config.h`
  - added `#include "gpi/arm/nordic/nrf528xx/platform_internal.h"` in `trafficbench/target/nrf52840/radio_queues_custom.h` to add back macros for trafficbench
  - added `#define LED_SYNC GPI_LED_0` for our target `#elif GPI_ARCH_IS_BOARD(TUDNES_SHEPHERD_NRF52840FRAM_V13)` in `trafficbench/scheduler.c`

## Usage on the testbed

on server - prereq:

```shell
cd ~
git clone https://github.com/nes-lab/shepherd-tools
cd shepherd-tools/extr

python3 gen_energy_envs.py
python3 gen_firmwares.py
python3 gen_rf_survey.py
# current firmware is now in /var/shepherd/content/fw/, accessible by all observers
# task is also accessible for all observers, but in our case we send it out via herd-tool
```

for the actual run:

```Shell
shepherd-herd -v run -a /var/shepherd/content/task/nes_lab/tasks_rf_survey.yaml
# this takes ~ 8min and will exit after. Then we collect the data
scp
```

scp /var/shepherd/recordings/

## TODO

- vary send-power (?)
- look for other IO used by TB
  - gpi_button_read() in main.c
  - gpi_led_toggle() in main.c
  - gpi_led_on() & gpi_led_off() in scheduler.c
  - LED_SYNC, GPI_LED_2
  - GPI_BUTTON_SIG1, GPI_BUTTON_1
- py:
  - filter_log.py and more
  - make code usable by other py-code
  - modularize + make testable
- speed up loop
  - 1 ms tx-delay
  - 3 ms tx-timeout
  - 15 - 50 ms sleep
  - factor in TRX_PRE_DELAY and _POST_DELAY
- packet-content: all random data might improve prx-consistency

## Source

<https://gitlab.com/nes-lab/trafficbench>

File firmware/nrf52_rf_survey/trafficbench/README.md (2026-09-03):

# TrafficBench

**NOTE**: this is a stripped copy of <https://github.com/nes-lab/TrafficBench> with small changes (node ID + X, described in readme one dir above).

---

TrafficBench is a tool suite for the experimental exploration of concurrent packet transmissions
and their consequences (physical layer effects) in low-power wireless networks. It integrates
[RSSISpy](https://gitlab.com/nes-lab/rssispy), a software module that enables continuous RSSI
measurements with bit-level time resolution, with a scheduling framework that provides a specialized,
easy-to-use language to implement communication test patterns. The latter offloads the user from
demanding implementation tasks like time-critical interrupt service routines, network bootstrapping,
synchronization, and efficient data logging. Thus, TrafficBench greatly simplifies the experimentation
with different traffic patterns and enables an in-depth inspection of the resulting effects.

TrafficBench consist of two major parts:

* A firmware that runs on the network nodes. Currently, TrafficBench supports Nordic
  Semiconductor [nRF52840](https://www.nordicsemi.com/Products/nRF52840) devices in
  Bluetooth Low Energy (BLE) mode.

* Python scripts that can be used to extract, analyze, and visualize the recorded data.

To learn more about TrafficBench, please read on. You can also have a look at our
[EWSN'22 demo abstract](https://nes-lab.org/wordpress/wp-content/uploads/2022/08/herrmann22trafficbench.pdf)
to gain an impression.

## Installation

In the following we focus on Linux. However, the main host tools are written in Python,
and we use the Python-based [Xonsh](https://xon.sh) shell for helper scripts, so installing
TrafficBench on other platforms should not be a big deal. On Windows, you should make
sure that `*.py` files are started with Python and `*.xsh` files with Xonsh, respectively.
You can also use the [Windows Subsystem for Linux](https://docs.microsoft.com/en-us/windows/wsl/about).

Installation steps:

1. Install [SEGGER Embedded Studio for ARM](https://www.segger.com/downloads/embedded-studio/#ESforARM) (SES).[^fn-ses]
   In our tests we have used SES version V6.34.
   You do not need the nRF Connect SDK.
   Depending on your test environment, you may need the
   [nRF Command Line Tools](https://www.nordicsemi.com/Products/Development-tools/nrf-command-line-tools)
   to program the target devices.

2. Set up a [Python 3](https://www.python.org/) environment (we have used Python 3.8 for our tests).
   We recommend to use a Python virtual environment, which can be
   created with `python3 -m venv <name_of_virtualenv>`
   and activated with `source <path_to_virtualenv>/bin/activate`.

3. Create a project directory and clone this repository into it:
   `git clone https://gitlab.com/nes-lab/trafficbench.git`.

4. Go to subfolder `host` and install all required Python modules:
   `pip install -r requirements.txt`.

After these steps, you should be able to start SES (start menu), Xonsh (`xonsh`),
ViTables (`vitables`), and Glue (`glue.xsh` in the `host` subfolder).

[^fn-ses]: SES is free for Nordic customers,
  see [news @ Segger](https://www.segger.com/news/segger-embedded-studio-ide-now-free-for-nordic-sdk-users/)
  and [tools-info @ nordic](https://www.nordicsemi.com/Products/Development-tools/Segger-Embedded-Studio).

## Usage

### Firmware

The task of the TrafficBench firmware is to implement a user-defined communication schedule
and to log all related data (events, transmitted and received packets, RSSI data streams, etc.)
to the UART terminal. Here, "implement" means to do everything that is needed to realize the
schedule, i.e., network wake-up, clock and state synchronization, and schedule program execution.

The firmware is ready to use in the sense that providing the schedule of interest (formulated
in the specialized language, see below) is enough
to be able to compile and run the firmware with the specific schedule.
To demonstrate the process, the source code comes with a tutorial schedule that can be used
to test the tool chain and run a simple test on a few Nordic
[nRF52840 DK](https://www.nordicsemi.com/Products/Development-hardware/nRF52840-DK)
development boards forming a small wireless network (using three boards is perfect, but even
a single board is enough to test the tool chain).
To do so, use the following steps:

1. Start SES and open the project [`target/nrf52840/project_ses/TrafficBench.emProject`](target/nrf52840/project_ses/TrafficBench.emProject).

2. Make sure to select "Release" as the active configuration (do not use "Release_FlockLab").
   Compile the project and program the executable into all boards.

3. For each board: Open a terminal (UART settings 230400,8,N,1, hardware flow control enabled).
   Press the reset button on the board and test if you see some output at the terminal.

   In case of problems, temporarily disable hardware flow control by setting
   `GPI_ARM_NRF_STDOUT_UART_FLOWCONTROL_MODE` to 0 in [`config.h`](target/nrf52840/project_ses/config.h)
   and try again. If hardware flow control is the reason for problems, then re-enable it and find out
   how to configure the terminal correctly (e.g. with PuTTY you can use -sercfg "230400,8,n,1,D").
   *Do not run the firmware without flow control on nRF52840 DK boards* because this can lead to
   awkward data losses.

4. You will be asked for a node ID at each terminal. Provide a unique ID for each board starting from 1, 2, ...

   The ID is stored in the device's UICR area, so it is kept persistent and not asked for again
   (also after re-programming). If you want to set a new ID, keep Button 1 pressed during boot-up,
   which enforces the ID prompt. See [`main.c`](target/nrf52840/main.c) for the details.

5. When everything is set up, press Button 1 at node 1. This starts communication and generates
   output at all terminals.

To evaluate the data with the TrafficBench host tools, you need to log the UART output of each
node to one or more files (e.g. one file per node). We do not provide any scripts for this task
because the right way to do it depends on your setup and the used terminal program (e.g. with
PuTTY you can use the command line option `-log <filename>`).
Public testbeds like [FlockLab](https://www.flocklab.ethz.ch) do it automatically (if UART
logging is turned on in the test configuration).

## Research

TrafficBench has been developed in the [Networked Embedded Systems Lab](https://nes-lab.org)
at [TU Dresden](https://tu-dresden.de) and [University of Freiburg](https://uni-freiburg.de/en/).
Please visit <https://nes-lab.org> to find out more.

---

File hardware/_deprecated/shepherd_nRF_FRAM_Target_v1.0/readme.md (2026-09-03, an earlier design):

# nRF52 & MSP430 FRAM Target V1.0

Shared pins between MCUs

| SHP-HDR | Dir   | Riotee   | nRF52  | msp430  | Description                 |
|---------|-------|----------|--------|---------|-----------------------------|
| GPIO0   | <-A-> | GPIO.7   | P0.11  | P5.3    | msp.B1.PSel                 |
| GPIO1   | <-A-> | GPIO.8   | P0.13  | P5.2    | msp.B1.CLK                  |
| GPIO2   | <-A-> | GPIO.2   | P0.04  | P2.3    | msp.A1.PSel                 |
| GPIO3   | <-A-> | GPIO.3   | P0.05  | P2.4    | msp.A1.CLK                  |
| GPIO4   | <--   | GPIO.4   | P1.09  | P4.6    |                             |
| GPIO5   | <--   | GPIO.5   | P0.26  | P3.6    |                             |
| GPIO6   | <--   | GPIO.6   | P1.03  | PJ.6    |                             |
| GPIO7   | <--   | GPIO.1   | P0.08  | P2.5    | UART Target-TX, msp.A1.CoPi |
| GPIO8   | <-B-> | GPIO.0   | P0.21  | P2.6    | UART Target-RX, msp.A1.CiPo |
| BATOK   | -->   | PG_H     | P0.07  | P5.5    |                             |
| prog11  | -->   | SWD.CLK  | swdclk | -       |                             |
| prog12  | <-C-> | SWD.IO   | swdio  | -       |                             |
| prog21  | -->   | SBW.CLK  | -      | sbwtck  |                             |
| prog22  | <-D-> | SBW.IO   | -      | sbwtdio |                             |
|         |       | LED.0    | P0.16  | P5.1    |                             |
|         |       | LED.1    | P0.12  | P5.0    |                             |
|         |       | LED.2P   | P0.03  | PJ.0    |                             |
|         |       | I2C.SCL  | P1.08  | P6.5    |                             |
|         |       | I2C.SDA  | P0.06  | P6.4    |                             |
|         |       | RTC.INT  | P0.30  | P7.3    |                             |
|         |       | C2C.CLK  | P0.18  | P1.5    |                             |
|         |       | C2C.CoPi | P0.17  | P2.0    |                             |
|         |       | C2C.CiPo | P0.14  | P2.1    |                             |
|         |       | C2C.PSel | P0.22  | P1.4    |                             |
|         |       | C2C.GPIO | P0.15  | PJ.2    |                             |

**Note**:

- SHP-HDR Spec of Cape V2.4
- Pins P[3:12] on Target-Header of V1.0 are GPIO[0:8] & BATOK

## Verifying the PCBs

- first do a visual inspection (both sides)
  - backside should be complete
  - front side can have two caps DNP (C14 & C9 in the middle)

### Assembly

- solder the 2x9-Pin-Header

### First Powerup

- 2 mA @ 3V without programming on V_target
- 0 mA @ 3V on 3V-Input

### Software-Prereqs

**NOTE**: all further tests are done on BBone

```Shell
cd ~
git clone https://github.com/nes-lab/shepherd-tools
cd shepherd-tools
git checkout dev
git pull

python3 ./extra/gen_firmwares.py
sudo python3 ./extra/gen_experiments.py
```

Put Target on BBone with Target on Port 1!

### Test all GPIO & LEDs

First test all used gpio with this fw-combo (msp toggles, nrf watches and reports via uart):

```Shell
sudo shepherd-sheep program -p A -m 1 -v 3 -t nrf52 extra/content/nrf52_testable/build.hex
sudo shepherd-sheep program -p A -m 2 -v 3 -t msp430 extra/content/msp430_testable/build.hex
sudo shepherd-sheep target-power -p A -v 3 --on
# new
sudo shepherd-sheep run /etc/shepherd/target_device_test1.yaml
```

NOTE: best done with interconnector that only routes: pwr1, serial, programming-pins, pwr2
Check UART output with logic analyzer or in shepherd recording.
Behavior is described in [the firmware-directory](https://github.com/nes-lab/shepherd-targets/tree/main/firmware/nrf52_testable).

### Testing the Radio

```Shell
sudo shepherd-sheep program -p A -m 1 -v 3 -t nrf52 extra/content/nrf52_rf_test/build.hex
sudo shepherd-sheep program -p A -m 2 -v 3 -t msp430 extra/content/msp430_deep_sleep/build.hex
sudo shepherd-sheep target-power -p A -v 3 --on
# new
sudo shepherd-sheep run /etc/shepherd/target_device_test2.yaml
```

Behavior is described in [the firmware-directory](https://github.com/nes-lab/shepherd-targets/tree/main/firmware/nrf52_rf_test).

### Testing Power-consumption during sleep

```Shell
sudo shepherd-sheep program -p A -m 1 -v 3 -t nrf52 extra/content/nrf52_deep_sleep/build.hex
sudo shepherd-sheep program -p A -m 2 -v 3 -t msp430 extra/content/msp430_deep_sleep/build.hex
# new
sudo shepherd-sheep run /etc/shepherd/target_device_test3.yaml
```

-> Overview / Results for manufactured PCBs moved to [doc_testbed](https://github.com/orgua/shepherd-v2-planning/tree/main/doc_testbed)

## Bugs, Changes, Improvements

### Changes after v1.0

- nrf module - trace cross / lines should be realigned
  - silk is more correct
  - fix on short side larger (~.5mm in)
  - result: set .4 mm in, crosses are 1.3 mm (X&Y) away from edge-pads
- 240R all same orientation? -> easier placing
- there are two different 1uF -> >4V, <<25 V, 0402 is wanted
- name LEDs

-> implemented in v1.1

### v1.1

Design-files are in [their directory](https://github.com/nes-lab/shepherd-targets/tree/main/hardware/shepherd_nRF_FRAM_Target_v1.1) - skipped

### v1.2

Design-files are in [their directory](https://github.com/nes-lab/shepherd-targets/tree/main/hardware/shepherd_nRF_FRAM_Target_v1.2).

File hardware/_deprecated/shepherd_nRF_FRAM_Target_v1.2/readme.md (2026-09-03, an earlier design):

# nRF52 & MSP430 FRAM Target V1.2

Shared pins between MCUs and Observer, **Cape V2.5 (not produced yet)**

| SHP-HDR  | Dir   | Riotee   | nRF52  | msp430  | Description                 |
|----------|-------|----------|--------|---------|-----------------------------|
| GPIO0    | <-A-> | GPIO.0   | P0.21  | P2.6    | UART Target-RX, msp.A1.CiPo |
| GPIO1    | <-B-> | GPIO.1   | P0.08  | P2.5    | UART Target-TX, msp.A1.CoPi |
| GPIO2    | <-C-> | GPIO.2   | P0.04  | P2.3    | msp.A1.PSel                 |
| GPIO3    | <-C-> | GPIO.3   | P0.05  | P2.4    | msp.A1.CLK                  |
| GPIO4    | <-C-> | GPIO.4   | P1.09  | P4.6    |                             |
| GPIO5    | <-C-> | GPIO.5   | P0.26  | P3.6    |                             |
| GPIO6    | <--   | GPIO.6   | P1.03  | PJ.6    |                             |
| GPIO7    | -->   | GPIO.7   | P0.11  | P5.3    | msp.B1.PSel                 |
| GPIO8    | <--   | GPIO.8   | P0.13  | P5.2    | msp.B1.CLK                  |
| GPIO9    | -->   | GPIO.9   | P0.16  | P5.1    | msp.B1.CiPo                 |
| PwrGoodL | -->   | PG_L     | P0.23  | P5.4    |                             |
| PwrGoodH | -->   | PG_H     | P0.07  | P5.5    |                             |
| prog11   | -->   | SWD.CLK  | swdclk | -       |                             |
| prog12   | <-A-> | SWD.IO   | swdio  | -       |                             |
| prog21   | -->   | SBW.CLK  | -      | sbwtck  |                             |
| prog22   | <-B-> | SBW.IO   | -      | sbwtdio |                             |
|          | -     | LED.0    | P0.12  | P5.0    | Riotee GPIO.10, msp.B1.CoPi |
|          | -     | LED.2P   | P0.03  | PJ.0    |                             |
|          | -     | I2C.SCL  | P1.08  | P6.5    |                             |
|          | -     | I2C.SDA  | P0.06  | P6.4    |                             |
|          | -     | RTC.INT  | P0.30  | P7.3    |                             |
|          | -     | C2C.CLK  | P0.18  | P1.5    | msp.A0.CLK                  |
|          | -     | C2C.CoPi | P0.17  | P2.0    | msp.A0.CoPi                 |
|          | -     | C2C.CiPo | P0.14  | P2.1    | msp.A0.CiPo                 |
|          | -     | C2C.PSel | P0.22  | P1.4    | msp.A0.PSel                 |
|          |       | C2C.GPIO | P0.15  | PJ.2    |                             |

**Note**:

- SHP-HDR Spec of Cape V2.5
- Testbed has still v2.4, 2024-08 - see table for target v1.0

## Verifying the PCBs

- first do a visual inspection (both sides)
  - backside should be complete
  - front side can have two caps DNP: big C14 @RTC & C9 in the middle (SW of MSP430)

### Assembly

- solder the 2x9-Pin-Header

### First Powerup

- 2 mA @ 3V on V_target without programming
- 0 mA @ 3V on 3V-Input

### Software-Prereqs

**NOTE**: all further tests are done on BBone

```Shell
cd ~
git clone https://github.com/nes-lab/shepherd-tools
cd shepherd-tools
git checkout dev
git pull

python3 ./extra/gen_firmwares.py
sudo python3 ./extra/gen_experiments.py
```

Put Target on BBone with Target on Port 1!

### Test all GPIO & LEDs

First test all used gpio with this fw-combo (msp toggles, nrf watches and reports via uart):

```Shell
sudo shepherd-sheep program -p A -m 1 -v 3 -t nrf52 /var/shepherd/content/fw/nes_lab/nrf52_testable/build.hex
sudo shepherd-sheep program -p A -m 2 -v 3 -t msp430 /var/shepherd/content/fw/nes_lab/msp430_testable/build.hex
sudo shepherd-sheep target-power -p A -v 3 --on
# new
sudo shepherd-sheep run /etc/shepherd/target_device_test1.yaml
```

NOTE: best done with interconnector that only routes: pwr1, serial, programming-pins, pwr2
Check UART output with logic analyzer or in shepherd recording.
Behavior is described in [the firmware-directory](https://github.com/nes-lab/shepherd-targets/tree/main/firmware/nrf52_testable).

### Testing the Radio

```Shell
sudo shepherd-sheep program -p A -m 1 -v 3 -t nrf52 /var/shepherd/content/fw/nes_lab/nrf52_rf_test/build.hex
sudo shepherd-sheep program -p A -m 2 -v 3 -t msp430 /var/shepherd/content/fw/nes_lab/msp430_deep_sleep/build.hex
sudo shepherd-sheep target-power -p A -v 3 --on
# new
sudo shepherd-sheep run /etc/shepherd/target_device_test2.yaml
```

Behavior is described in [the firmware-directory](https://github.com/nes-lab/shepherd-targets/tree/main/firmware/nrf52_rf_test).

### Testing Power-consumption during sleep

```Shell
sudo shepherd-sheep program -p A -m 1 -v 3 -t nrf52 /var/shepherd/content/fw/nes_lab/nrf52_deep_sleep/build.hex
sudo shepherd-sheep program -p A -m 2 -v 3 -t msp430 /var/shepherd/content/fw/nes_lab/msp430_deep_sleep/build.hex
# new
sudo shepherd-sheep run /etc/shepherd/target_device_test3.yaml
```

## Assembled Units

- visual inspection -> reflow fails:
  - A: crystal on ABx & MSP, one R240 on back
  - B: crystal on MSP,
  - C: crystal on ABx & nRF
- PowerUp
  - C: 3-4 mA on VTarget, instead of 2 mA
- Programming -> A, B fully responding
- Testable-FW
  - many shorts or permanent-high GPIO
- RF-Test - 1 m away in Doughnut-Pattern & 1 m above
  - A: -56 dBm in, -49 dBm above (SMA-Port loosely attached)
  - B: -56 dBm in, -48 dBm above
  - C: -50 dBm in, -52 dBm above
  - C: -47 dBm above (soldered SMA)
  - Target 7 with Stub-Antenna: -64 dBm in, -62 dBm above
  - Target 18 with Chip-Antenna: -67 to -72 dBm in, -69 to -72 dBm above
  - Various far points in flat show: 80-100 with chip antenna, 85-90 with stub, 65-83 with dedicated Antenna

```A
GPIO WATCHER
Missing: 2 12         -> GPIO3, LED2
Always:  5 8 10 [14]  -> GPIO6, GPIO9, PH
              1
          1   1
        1 1   1
     1  1 1   1
     1  1 11  1
1    1  1 1   1
 1   1  1 1   1
   1 1  1 1   1
    11  1 1   1
     11 1 1   1
     1 11 1   1
     1  1 1   1
     1  111   1
     1  1 1   1
     1  1 1
     1  1 1  1
     1  1 1   1
     1  1 1     1
     1  1 1      1
     1  1 1       1
     1  1 1        1
     1  1 1         1
     1  1 11
     1  1 1
```

```B
GPIO WATCHER
Missing: 2 12 15
Always:  5 8 9 13 [14]
     1       11
     1  1    11
     1  1 1  11
     1  1    11
     1  11   11
     1  11 1 11
1    1  11   11
 1   1  11   11
   1 1  11   11
    11  11   11
     1  11   11
     11 11   11
     1 111   11
     1  11   11
     1  111  11
     1  11   11
     1  11   1
     1  11   11
     1  11   1
     1  11   1  1
     1  11   1   1
     1  11   1    1
     1  11   1     1
     1  11   1      1
     1  11 1 1
     1  11   11
     1  11 1 11
```

```C
GPIO WATCHER
Missing: none
Always:  [3] 5 9 [13]
   1
   1     1
   1 1   1
   1 1   1 1
   1 1   1
   1 1   1  1
   1 1   1  11
   1 1   1   1
   1 1   1  11
   1 1   1   1
   1 1   1  11
   1 1   1   1
     1   1   1
1    1   1   1
     1   1   1
     1   1  11
     1   1   1
 1   1   1   1
     1   1   1
     1   1  11
     1   1   1
  1  1   1   1
     1   1   1
     1   1  11
     1   1   1
   1 1   1   1
     1   1   1
     1   1  11
     1   1   1
    11   1   1
     1   1   1
     1   1  11
     1   1   1
     1   1  11
     1   1   1
     11  1   1
     1   1   1
     1   1  11
     1   1   1
     1 1 1   1
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
Received all 21 shared pins!!
```

## Bugs, Changes, Improvements

### Changes from prev Version

- two bat-status pins from cape would be better
  - goal: offer hysteresis - working good for riotee so far
  - second goal: compatibility with riotee-SDK for targets
- shared gpio would benefit from external PU/PD-Resistors, so current mcu-code can be more independent
  - problem: msp430 is reacting with high currents for floating pins
  - current solution: activate internal PD-Res in msp430 - at least for our sleep- & FRAM-firmware
- add a system to identify pcb? OW-nodeid or i2c-rom?
- ditch PAN1780 module to allow an external antenna (rf-performance of pan-module is sub-par)

#### Details

- additional parts to order
  - rpi pico - <https://www.mouser.de/ProductDetail/Raspberry-Pi/SC0915?qs=T%252BzbugeAwjgnLi4azxXVFA%3D%3D>
  - rpi pico H <https://www.mouser.de/ProductDetail/Raspberry-Pi/SC0917?qs=T%252BzbugeAwjjvYEYcRJk%252Bxw%3D%3D>
  - rpi pico W <https://www.mouser.de/ProductDetail/Raspberry-Pi/SC0918?qs=T%252BzbugeAwjj9dgdBLZSmdg%3D%3D>
  - rpi 5 <https://www.mouser.de/ProductDetail/Raspberry-Pi/SC1112?qs=HoCaDK9Nz5c86n0i5EQ%2FPA%3D%3D>
  - Antenna <https://www.mouser.de/c/passive-components/antennas/?q=antenna%20sma&minimum%20frequency=2.4%20GHz%7C~2.41%20GHz~~2.45%20GHz&instock=y&NewSearch=1&rp=passive-components%2Fantennas%7C~Minimum%20Frequency&sort=pricing>
  - Antenna refinement <https://www.mouser.de/c/passive-components/antennas/?q=antenna%20sma&antenna%20connector%20type=SMA%20Connector%7C~SMA%20Male~~SMA%20Plug&maximum%20frequency=2.48%20GHz~~2.5%20GHz&minimum%20frequency=2.4%20GHz%7C~2.41%20GHz~~2.45%20GHz&instock=y&sort=pricing&NewSearch=1&rp=passive-components%2Fantennas%7C~Minimum%20Frequency%7C~Maximum%20Frequency%7C~Antenna%20Connector%20Type>
  - HDR2x10 RM2 737-2PH2-20-UA
  - rare cape-parts
- gpio.9 is now dedicated gpio and not bat_OK anymore (free from LED.0)
- gpio.10 was LED.1, is now LED.0
- `VCAP_SENSE` was floating, now V_Target
  - <https://github.com/NessieCircuits/Riotee_MSP430Fram/blob/main/src/main.c>
  - <https://github.com/NessieCircuits/Riotee_SDK/blob/main/core/include/riotee.h>
  - `PIN_VCAP_SENSE`, `AIN_VCAP_SENSE` are configured, but unused by riotee (FRAM-FW & SDK)
- `PIN_MAX_INT` is left floating (unchanged) as it is configured, but unused by SDK & not avail on target
- discrete nRF52 IC,
  - Riotee: NRF52833-CJAA (+direction finding)
  - Targetv11: 52840 (+matter) -> Choose this one
  - CJAA => WLCS 3.2x3.2 mm
  - QIAA => aQFN73 7x7mm -> Choose this one
  - QDAA => QFN40
  - CFAA => WLCSP-44
- switch ClockCrystal from 20 ppm to 5 ppm
- LED.1 is unused -> removed
- 2x10 HDR -> RM2.0mm
- re-aligned gpios between observer & target
- nRF - 2 crystals
- also share threshold-control + max-int between MCUs (with 470R)
- SMA or uFL? -> SMA
- adapt capacities for crystals
- nRF - Antenna path - 630 um on L1/L4 are 50 Ohms,
  - both ant-traces are < 5 mm and therefore well below 10% of 2.4 GHz wavelength
- add antenna to schematic
- replace msp430 128kb (-FR5962) with riotees 256kb (-FR5994),

Skipped:

- PD-Res for internal Pins - 10 M?

### Riotee-SDK-patching

- target uses nRF52840 instead of Riotees -833
- main makefile specifies `NRF_DEV_NUM`
- Size of FRAM auto-adjust? -> main makefile `RIOTEE_RAM_RETAINED_SIZE`, `RIOTEE_STACK_SIZE`
- type of nRF relevant? -> main Makefile `NRF_DEV_NUM`

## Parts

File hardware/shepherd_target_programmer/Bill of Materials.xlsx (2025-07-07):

Comment | Designator | Footprint | LibRef | Quantity | Manufacturer | Manufacturer PN | Distributer | Distributer PN | Price n10 [€]
C_0402_1uF_10V_X7R | C1 | CAPC1005X06 | .C_0402_1uF_X7R_10V | 1 | Murata | GRM155C71A105KE11D | Mouser | 81-GRM155C71A105KE1D | 0.036
D_LED_0603_Amber | D1 | DIOM1608X02N Orange | .D_LED_0603_Amber | 1 | Wuerth | 150060AS75000 | Mouser | 710-150060AS75000 | 0.12
P_HSEC8-120-01-S-DV | P1 | P_HSEC8-120-01-S-DV | .P_HSEC8-120-01-S-DV | 1 | Samtec | HSEC8-120-01-L-DV-A-K-TR | Mouser | 200-HSEC812001LDVAKT | 3.17
P_RPI_PICO_40Pin | P2 | P_rpi_pico_R2.54mm | .P_RPI_PICO_40Pin | 1 | Raspberry Pi | SC0915 | Mouser | 358-SC0915 | 3,72
P_HDR_2x2_2.54mm_header | P3 | P_Pinheader_2x2_R2.54mm | .P_HDR_2x2_2.54mm_male | 1 | Amphenol | 861400042YO2319LF | Mouser | 649-86140042YO2319LF | 0.12
R_0402_1k | R1 | RESC1005X04 | .R_0402_1k | 1 | Panasonic | ERJ-2GEJ102X | Mouser | 667-ERJ-2GEJ102X | 0.02
R_0402_470R | R2, R3, R4, R5, R6, R7 | RESC1005X04 | .R_0402_470R_1% | 6 | Panasonic | ERJ-2RKF4700X | Mouser | 667-ERJ-2RKF4700X | 0.028
R_1206_2R_0.25% | R8 | RESC3116X06 Shunt | .R_1206_2R_0.25% | 1 | Yageo | RT1206CRD072RL | Mouser | 603-RT1206CRD072RL | 0.35

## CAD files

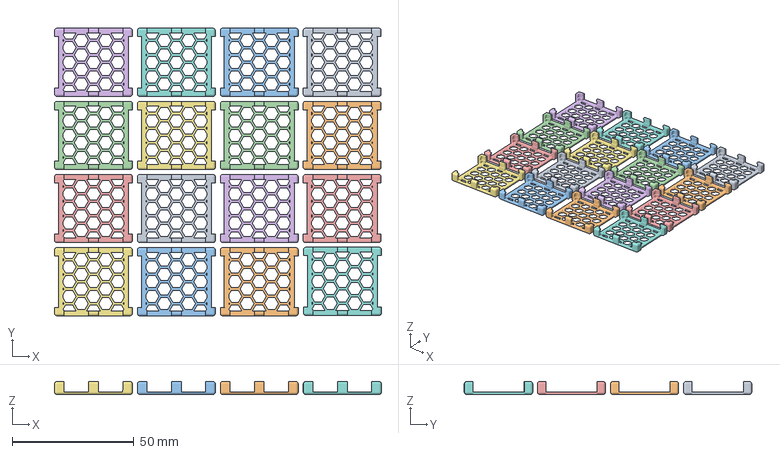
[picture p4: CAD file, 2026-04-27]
hardware/target_v1.3_cage/target_cage_PLA_x16.3mf
134.1 x 118.0 x 5.30 mm
target_v13_cage.stl x 16

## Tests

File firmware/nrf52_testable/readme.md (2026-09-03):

# nRF52 Testable

The app monitors shared GPIO pins and reports via uart upon detection.
This needs a second MCU that toggles these gpio (companion-firmware `/msp430_testable`).
Alternatively this FW can change the mode to toggling-behavior.

Other modes:

Print the index of the pin where the edge was detected over UART.
Simultaneously, it waits for incoming messages on the UART.
When receiving an ASCII encoded number between 0 and the number of configured pins,
the app sets the corresponding pin high for ~100us.

Edit the `pins` array and the UART pin definitions at the top of `src/main.c` to reflect your hardware.

## Functionality

### Mode 0 - Supervisor (default)

- monitor all shared GPIO and report activity via uart
- msp-testable-firmware is actor (gpio toggle, here mode 1)
- NOTE: requires special Header-Inter-connector that only routes pwr, uart tx, programming (pin 1, 2, 10, 13 - 18)
- NOTE 3: 115200 baud datarate

### Mode 1 - Actor

- Startup-Routine 1:
  - toggles LEDs, Pins on the shepherd target-port (without UART-TX), I2C pins, chip-to-chip (C2C) pins
  - blink / switch on each pin individually for 100 ms
- Startup-Routine 2: LEDs
  - switch each LED on for 100ms consecutive
  - (depending on node-id) >=8 repetitions
  - LED0:2 (Target v2.1)

### Mode >=2

- UART
  - P0_06 TX, _08 RX (Target v2.1, SDK)
  - listens and answers
  - should report when GPIOs are triggered
- GPIO
  - active: GPIO of shepherd target header (GPIO 0 to 6, 8, BATOK -> map to 0:8)
  - switch on for 100 us after receiving on UART ("(%u)\r\n")
- NOTE: 115200 baud datarate

## Example Output Mode 0

```uart
GPIO WATCHER (31 pins)
               56
0              56
               56
 1             56
               56
  2            56
               56
   3           56
               56
    4          56
               56
     5         56
               56
      6        56
               56
       7       56
               56
        8      56
               56
         9     56
               56
          0    56
               56
           1   56
               56
            2  56
               56
             3 56
               56
              456
               56
               567
               56
               56 8
               56
               56  9
               56
               56   0
               56
               56    1
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
Received all 31 shared pins!!
```

## Source

based on <https://github.com/geissdoerfer/shepherd-nrf52-demo>

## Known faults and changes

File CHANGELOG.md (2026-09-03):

# Changelog

## v0.6.2 - unreleased

- add firmware to benchmark and measure uart-throughput of the testbed
- doc improvements & fixes
- lint markdown-files

## v0.6.1

- extend node-count for rf-survey (trafficbench)
- switch from pipenv to uv / pip environments
- switch from pre-commit to prek
- audit GH workflows with zizmor

## v0.6.0

- extend documentation
- hardware - add more adapters (mostly for debug)
- hardware - add target-programmer (clone of riotee-board) that can program both MCUs on the target 1.3e and has an interface for UART
- change repo location and update references
- move firmwares into `/firmware`-subdir
- update deps and tooling

## v0.5.2

- add revised nRF-FRAM Target v1.3e (no functional changes)
- update GPI, which now supports this target
- adapt trafficbench / rf-survey and generate link-matrix
- deprecate old design-files (prior v1.3)
- update deps and tooling

## v0.5.1

- add documentation
- update deps
- fix QA

## v0.5.0

- adapt firmware to nRF-FRAM Target v1.3
- improve testing
- add new hardware
  - target v1.3, manufactured and tested
  - target v1.2 (skipped)
  - target adapter
  - debug adapter
  - target cage
- update & adapt documentation
- tooling
  - add templates for issues (bug, feature)
  - add dependabot-updater
- update deps
- add code of conduct

## v0.4.3

- last version to support nRF-FRAM Targets v1.1 & v1.0

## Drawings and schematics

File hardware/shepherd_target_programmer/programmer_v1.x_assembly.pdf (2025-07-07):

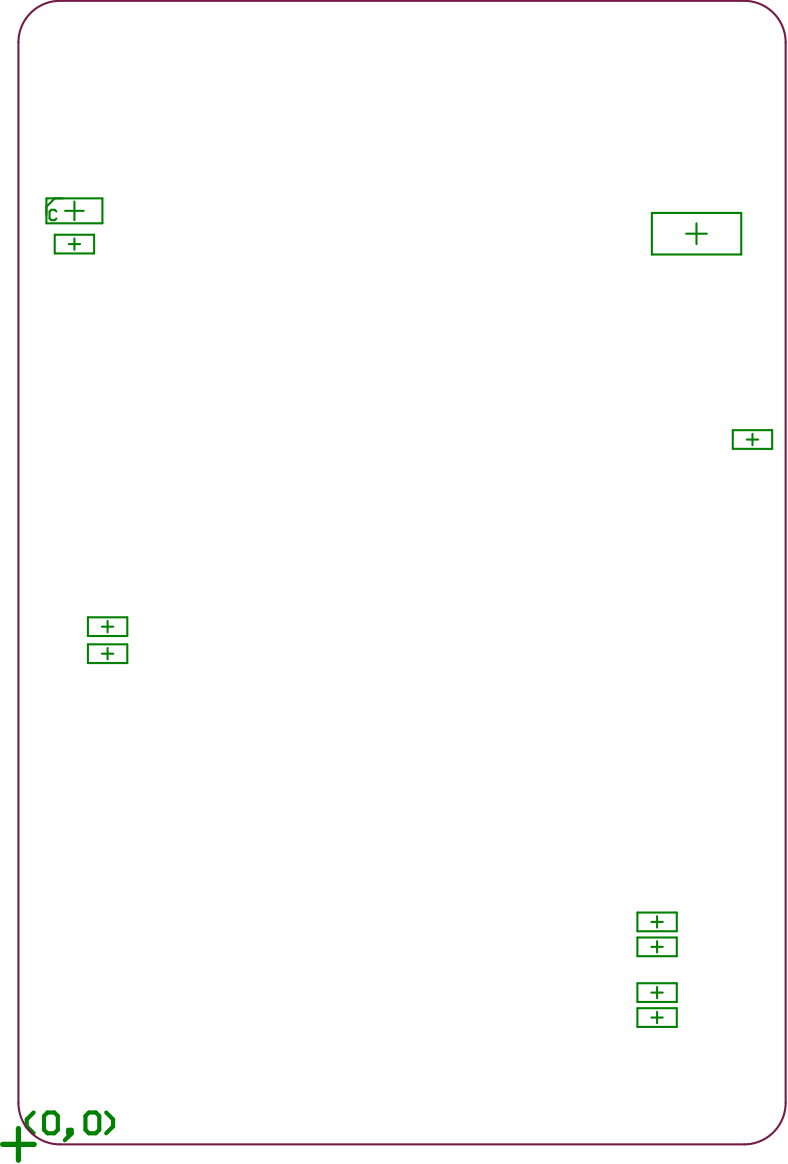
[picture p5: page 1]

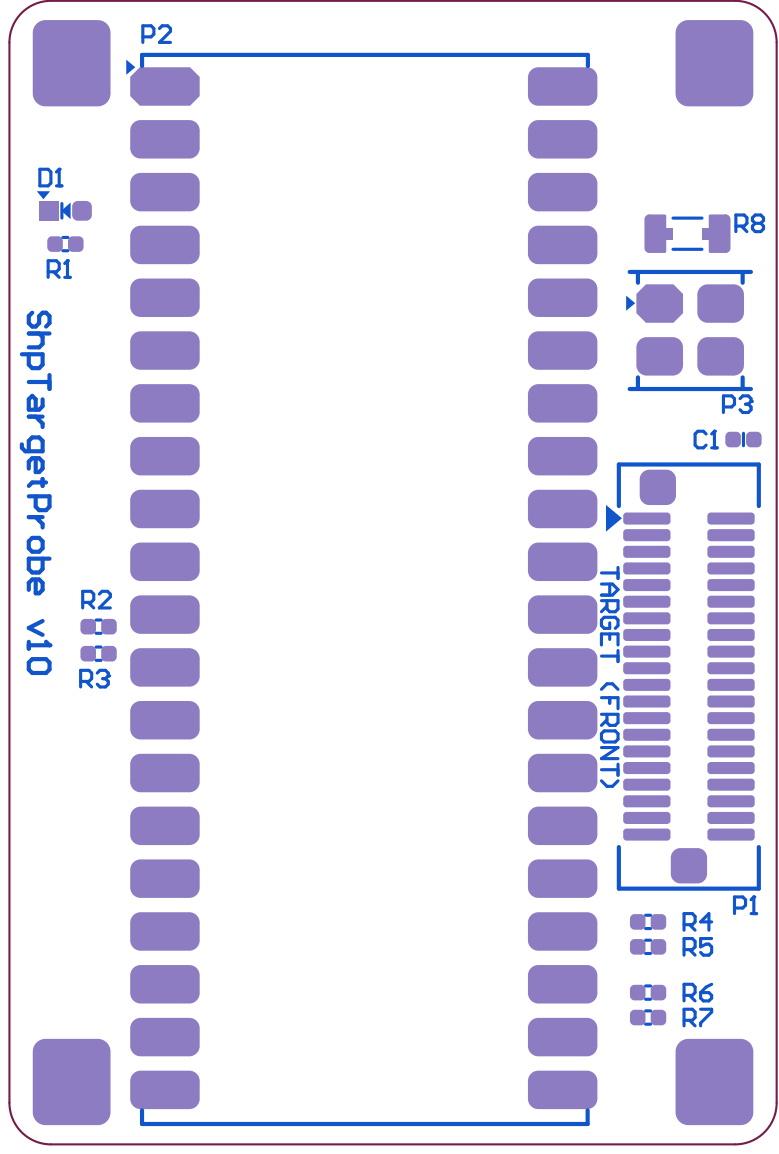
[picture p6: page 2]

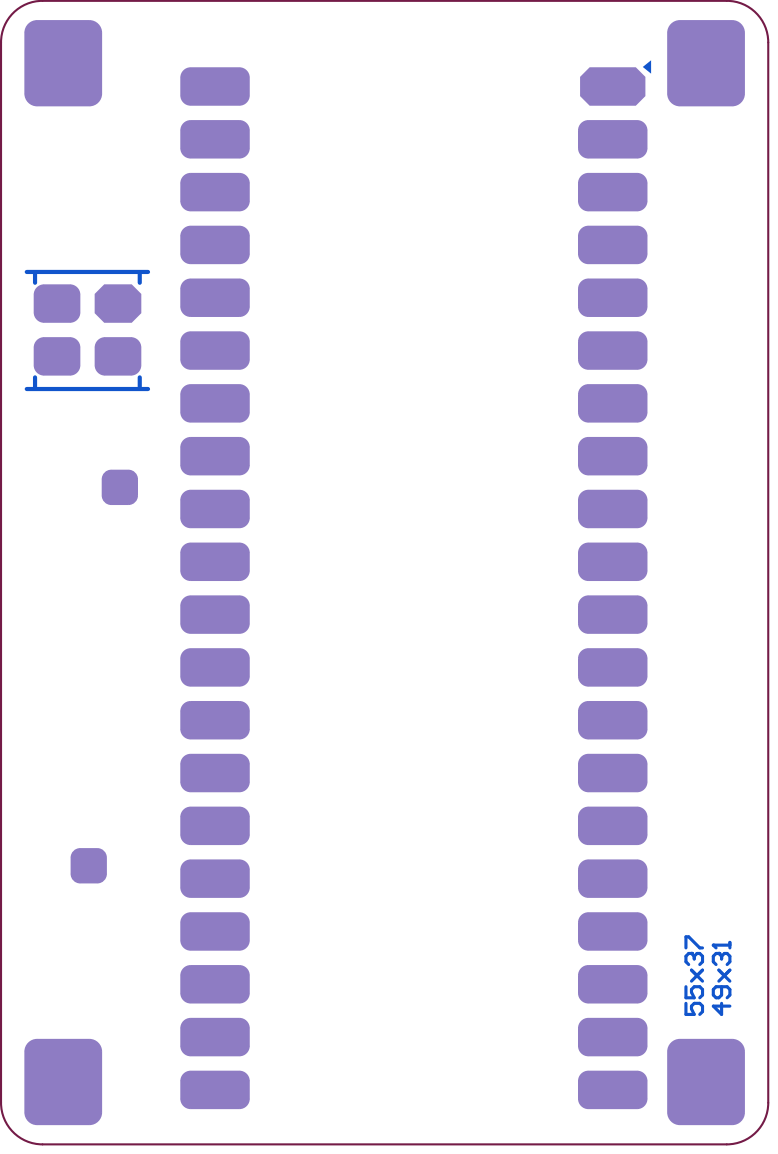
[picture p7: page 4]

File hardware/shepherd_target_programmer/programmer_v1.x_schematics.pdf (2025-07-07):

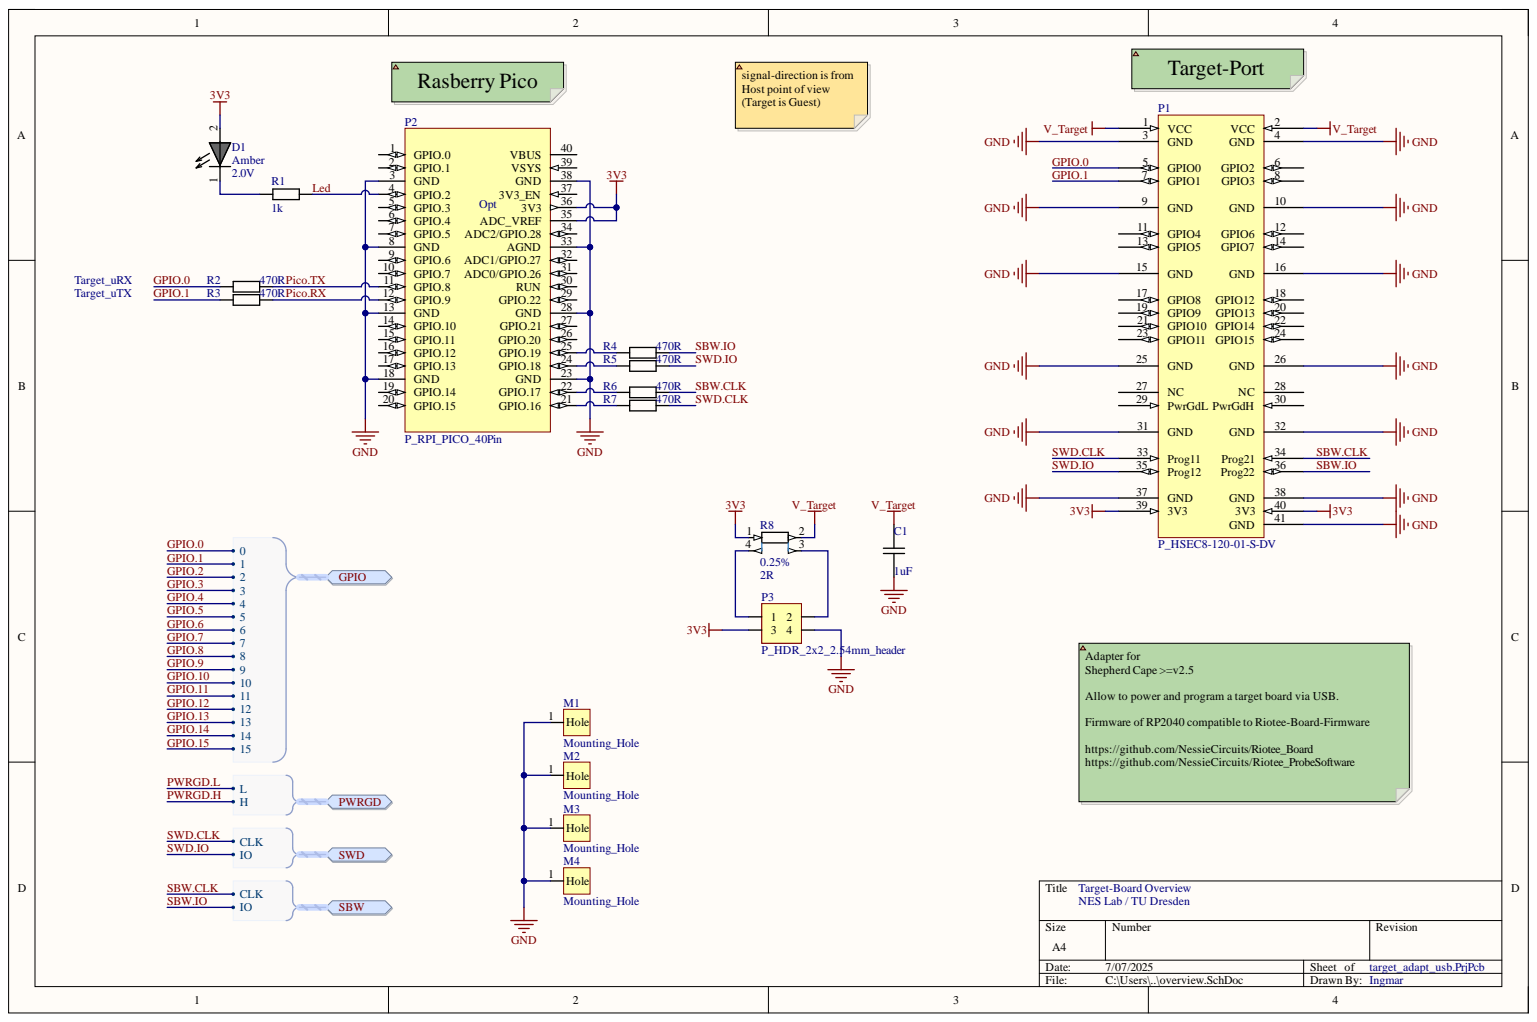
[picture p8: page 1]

9 1 0 1 1 | | 3 2 3 1 30 9 RUN 2 2 8

GPIO.0 GPIO.1 GPIO.2 GPIO.3 GPIO.4 GPIO.5 GPIO.6 GPIO.7 GPIO.8 GPIO.9 GPIO.1

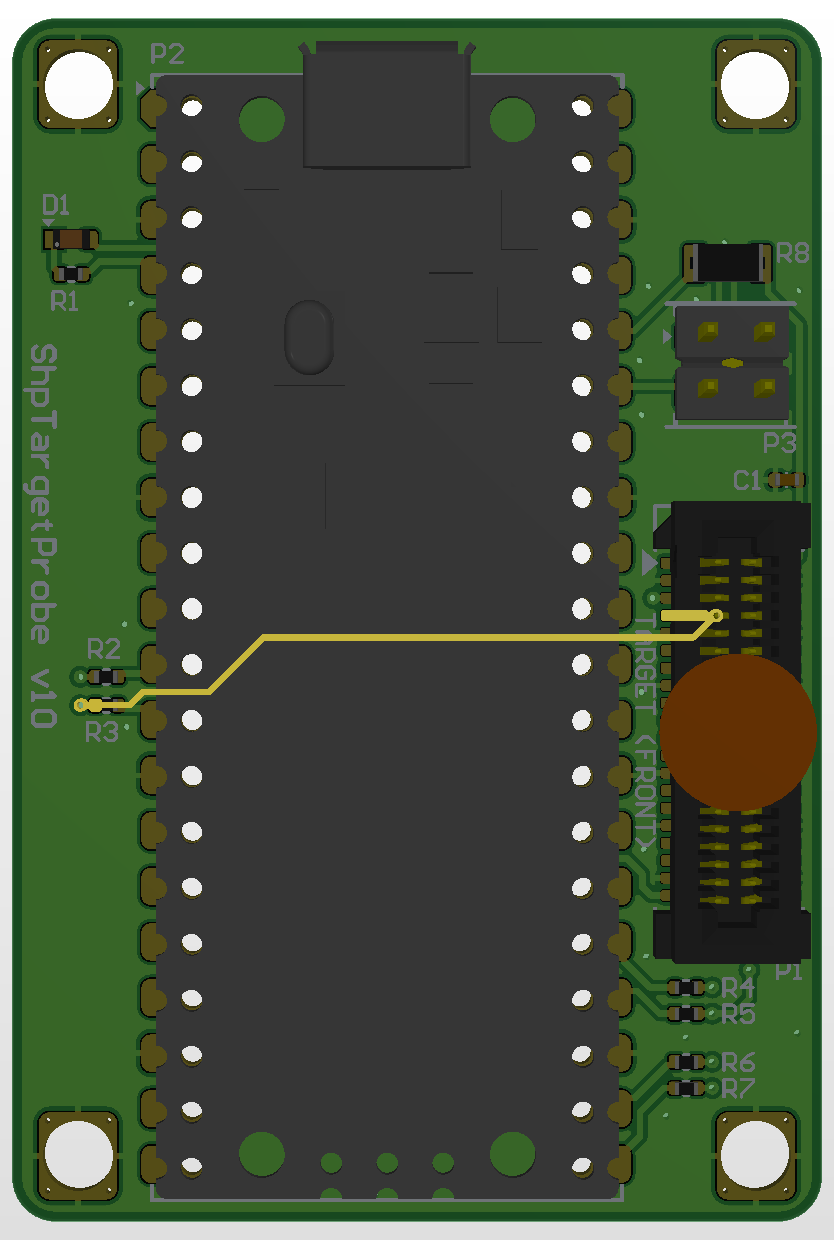
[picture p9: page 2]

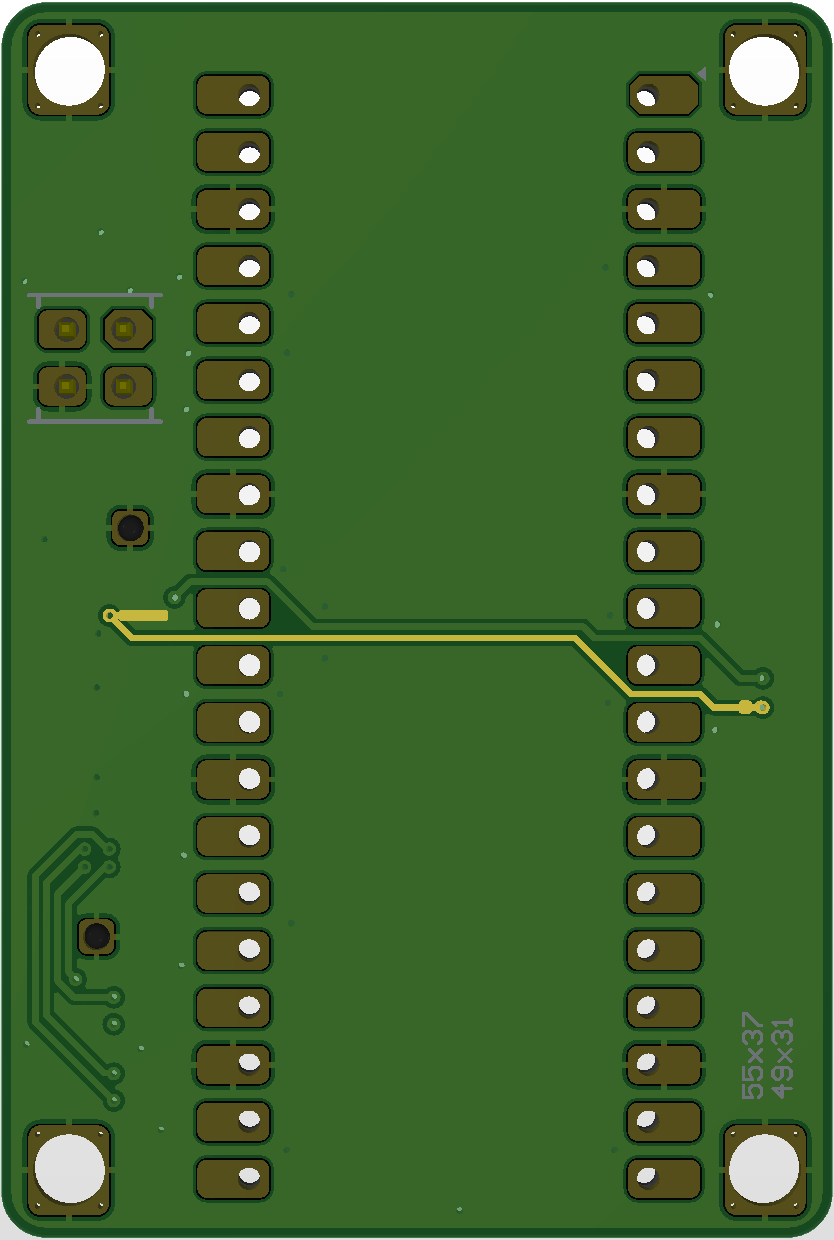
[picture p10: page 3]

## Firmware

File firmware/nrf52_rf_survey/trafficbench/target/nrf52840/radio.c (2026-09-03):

/***************************************************************************************************
 ***************************************************************************************************
 *
 *	Copyright (c) 2021 - 2022, Networked Embedded Systems Lab, TU Dresden
 *	All rights reserved.
 *
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
 *	THIS SOFTWARE IS PROVIDED BY THE COPYRIGHT HOLDERS AND CONTRIBUTORS "AS IS" AND
 *	ANY EXPRESS OR IMPLIED WARRANTIES, INCLUDING, BUT NOT LIMITED TO, THE IMPLIED
 *	WARRANTIES OF MERCHANTABILITY AND FITNESS FOR A PARTICULAR PURPOSE ARE
 *	DISCLAIMED. IN NO EVENT SHALL THE COPYRIGHT HOLDER BE LIABLE FOR ANY
 *	DIRECT, INDIRECT, INCIDENTAL, SPECIAL, EXEMPLARY, OR CONSEQUENTIAL DAMAGES
 *	(INCLUDING, BUT NOT LIMITED TO, PROCUREMENT OF SUBSTITUTE GOODS OR SERVICES;
 *	LOSS OF USE, DATA, OR PROFITS; OR BUSINESS INTERRUPTION) HOWEVER CAUSED AND
 *	ON ANY THEORY OF LIABILITY, WHETHER IN CONTRACT, STRICT LIABILITY, OR TORT
 *	(INCLUDING NEGLIGENCE OR OTHERWISE) ARISING IN ANY WAY OUT OF THE USE OF THIS
 *	SOFTWARE, EVEN IF ADVISED OF THE POSSIBILITY OF SUCH DAMAGE.
 *
 ***********************************************************************************************//**
 *
 *	@file					radio.c
 *
 *	@brief					radio transmit and receive functions including RSSISpy
 *
 *	@version				$Id$
 *	@date					TODO
 *
 *	@author					Carsten Herrmann
 *
 ***************************************************************************************************

 	@details

	TODO

 **************************************************************************************************/
//***** Trace Settings *****************************************************************************

#include "gpi/trace.h"

// message groups for TRACE messages (used in GPI_TRACE_MSG() calls)
#define TRACE_INFO    GPI_TRACE_MSG_TYPE_INFO
#define TRACE_WARNING GPI_TRACE_MSG_TYPE_WARNING
#define TRACE_ERROR   GPI_TRACE_MSG_TYPE_ERROR
#define TRACE_VERBOSE GPI_TRACE_MSG_TYPE_VERBOSE

// select active message groups, i.e., the messages to be printed (others will be dropped)
#ifndef GPI_TRACE_BASE_SELECTION
  #define GPI_TRACE_BASE_SELECTION (GPI_TRACE_LOG_STANDARD | GPI_TRACE_LOG_PROGRAM_FLOW)
#endif
#ifndef GPI_TRACE_USER_SELECTION
  #define GPI_TRACE_USER_SELECTION GPI_TRACE_LOG_USER
#endif
#if (GPI_TRACE_USER_SELECTION & GPI_TRACE_MSG_TYPE_VERBOSE)
  #define TRACE_USER_SELECTION (GPI_TRACE_USER_SELECTION | GPI_TRACE_LOG_FUNCTION_RETURN_MSG)
#else
  #define TRACE_USER_SELECTION GPI_TRACE_USER_SELECTION
#endif
GPI_TRACE_CONFIG(radio, GPI_TRACE_BASE_SELECTION | TRACE_USER_SELECTION);

//**************************************************************************************************
//**** Includes ************************************************************************************

#include "radio.h"

#include "gpi/clocks.h"
#include "gpi/interrupts.h"
#include "gpi/olf.h"
#include "gpi/platform.h"
#include "gpi/resource_check.h"
#include "gpi/tools.h"
#include GPI_PLATFORM_PATH(radio.h)

#include <nrf.h>

#include <stdint.h>

//**************************************************************************************************
//***** Local Defines and Consts *******************************************************************

// DEBUG_RSSI can be used to debug the RSSI sampling subsystem.
// It reduces the sampling rate and additionally outputs internal variables to the sample buffer.
#define DEBUG_RSSI 0

// use DEBUG_GPIO to connect internal events to GPIO pins (allows external monitoring)
#define DEBUG_GPIO 0

// sampling period in timer ticks
#if DEBUG_RSSI
  #define RSSI_SAMPLING_PERIOD 4096
#else
  #define RSSI_SAMPLING_PERIOD 16
#endif

//**************************************************************************************************
// resource assignments
// TODO: maybe move to a header file to simplify application-specific adaptions

#define MAIN_TIMER_INDEX         GPI_ARM_NRF_FAST_CLOCK_TIMER
#define RSSI_TIMER_INDEX         0
#define RSSI_TIMER2_INDEX        1
#define RSSI_TIMER3_INDEX        2

#define RSSI_MWU_REGION          0

// NOTE: could check if any of the pre-programmed PPI channels can be used
#define PPI_START                0
#define PPI_READY                1
#define PPI_ADDRESS              2
//#define PPI_PAYLOAD					3
#define PPI_END                  4
#define PPI_RSSI_START           5
#define PPI_RSSI_END             6
#define PPI_RSSI_MWU             7
#define PPI_RSSI_COUNT           8
#define PPI_TX_CONTROL           9 // can be shared with PPI_RSSI_... if not enough channels

// CC regs (CCI_ = CC index, CCR_ = CC reg)
// NOTE: CC[0] = GPI_ARM_NRF_FAST_CLOCK_CAPTURE_REG
// if there is a lack of CC regs: radio events could use same CC with timestamps saved in the radio ISR
#define CCI_MAIN_COMPARE         1
#define CCI_MAIN_START_READY_END 2
#define CCI_MAIN_ADDRESS         3
#define CCI_MAIN_RSSI_START      4
#define CCI_MAIN_RSSI            5
//#define CCI_MAIN_PAYLOAD			4

#ifdef DEBUG_GPIO
  #if GPI_ARCH_IS_BOARD(FLOCKLAB_nRF5)
    #define LED_RADIO_ISR      GPI_LED_INT1
    #define LED_MAIN_TIMER_ISR GPI_LED_INT2
    #define LED_RSSI_TIMER     GPI_LED_1
    #define LED_RSSI_ACTIVE    GPI_LED_2
    #define PPI_DEBUG1         10
    #define PPI_DEBUG2         11
    #define GPIOTE_DEBUG1      0
    #define GPIOTE_DEBUG2      1
  #elif GPI_ARCH_IS_BOARD(nRF_PCA10056)
    #define LED_RADIO_ISR      GPI_LED_3
    #define LED_MAIN_TIMER_ISR GPI_LED_4
    #define GPIO_DEBUG1_PORT   1
    #define GPIO_DEBUG1_PIN    10
    #define GPIO_DEBUG1_Px     CONCAT(NRF_P, GPIO_DEBUG1_PORT)
    #define GPIOTE_DEBUG1      0
  #endif
  #ifndef LED_RADIO_ISR
    #define LED_RADIO_ISR GPI_LED_NONE
  #endif
  #ifndef LED_MAIN_TIMER_ISR
    #define LED_MAIN_TIMER_ISR GPI_LED_NONE
  #endif
  #ifndef LED_RSSI_TIMER
    #define LED_RSSI_TIMER GPI_LED_NONE
  #endif
  #ifndef LED_RSSI_ACTIVE
    #define LED_RSSI_ACTIVE GPI_LED_NONE
  #endif
#endif

//**************************************************************************************************
// derived resource macros and resource reservations
// (for details see gpi/resource_check.h)

// TIMER0...TIMER2 have only 4 CCs -> MAIN_TIMER must be TIMER3 or TIMER4
ASSERT_CT_STATIC(MAIN_TIMER_INDEX >= 3, MAIN_TIMER_INDEX_must_be_3_or_4);

#define MAIN_TIMER          CONCAT(NRF_TIMER, MAIN_TIMER_INDEX)
#define MAIN_TIMER_IRQ      CONCAT(TIMER, MAIN_TIMER_INDEX, _IRQn)
#define MAIN_TIMER_ISR_NAME CONCAT(TIMER, MAIN_TIMER_INDEX, _IRQHandler)

GPI_RESOURCE_RESERVE_SHARED(NRF_TIMER, MAIN_TIMER_INDEX);

#define RSSI_TIMER           CONCAT(NRF_TIMER, RSSI_TIMER_INDEX)
#define RSSI_TIMER2          CONCAT(NRF_TIMER, RSSI_TIMER2_INDEX)
#define RSSI_TIMER3          CONCAT(NRF_TIMER, RSSI_TIMER3_INDEX)
#define RSSI_IRQ             CONCAT(TIMER, RSSI_TIMER_INDEX, _IRQn)
#define RSSI_ISR_NAME        CONCAT(TIMER, RSSI_TIMER_INDEX, _IRQHandler)
#define RSSI_TIMER2_IRQ      CONCAT(TIMER, RSSI_TIMER2_INDEX, _IRQn)
#define RSSI_TIMER2_ISR_NAME CONCAT(TIMER, RSSI_TIMER2_INDEX, _IRQHandler)

GPI_RESOURCE_RESERVE(NRF_TIMER, RSSI_TIMER_INDEX);
GPI_RESOURCE_RESERVE(NRF_TIMER, RSSI_TIMER2_INDEX);
GPI_RESOURCE_RESERVE(NRF_TIMER, RSSI_TIMER3_INDEX);
GPI_RESOURCE_RESERVE_SHARED(NRF_MWU);
GPI_RESOURCE_RESERVE(NRF_MWU_REGION, RSSI_MWU_REGION);
GPI_RESOURCE_RESERVE(NRF_TEMP);

#define PPI_CHEN_TX_MASK (BV(PPI_ADDRESS) | BV(PPI_END))
//#define PPI_CHEN_TX_MASK			(BV(PPI_ADDRESS) | BV(PPI_PAYLOAD) | BV(PPI_END))

#if defined(PPI_DEBUG2)
  #define PPI_CHEN_RX_MASK_EXTRA (BV(PPI_DEBUG1) | BV(PPI_DEBUG2))
#elif defined(PPI_DEBUG1)
  #define PPI_CHEN_RX_MASK_EXTRA BV(PPI_DEBUG1)
#else
  #define PPI_CHEN_RX_MASK_EXTRA 0
#endif
#define PPI_CHEN_RX_MASK                                                                           \
    (PPI_CHEN_TX_MASK | PPI_CHEN_RX_MASK_EXTRA | BV(PPI_READY) | BV(PPI_RSSI_START) |              \
     BV(PPI_RSSI_END) | BV(PPI_RSSI_MWU) | BV(PPI_RSSI_COUNT))

GPI_RESOURCE_RESERVE_SHARED(NRF_PPI);
GPI_RESOURCE_RESERVE(NRF_PPI_CH, PPI_START);
GPI_RESOURCE_RESERVE(NRF_PPI_CH, PPI_READY);
GPI_RESOURCE_RESERVE(NRF_PPI_CH, PPI_ADDRESS);
//GPI_RESOURCE_RESERVE(NRF_PPI_CH, PPI_PAYLOAD);
GPI_RESOURCE_RESERVE(NRF_PPI_CH, PPI_END);
GPI_RESOURCE_RESERVE(NRF_PPI_CH, PPI_RSSI_START);
GPI_RESOURCE_RESERVE(NRF_PPI_CH, PPI_RSSI_END);
GPI_RESOURCE_RESERVE(NRF_PPI_CH, PPI_RSSI_MWU);
GPI_RESOURCE_RESERVE(NRF_PPI_CH, PPI_RSSI_COUNT);
GPI_RESOURCE_RESERVE(NRF_PPI_CH, PPI_TX_CONTROL);
#ifdef PPI_DEBUG1
GPI_RESOURCE_RESERVE(NRF_PPI_CH, PPI_DEBUG1);
#endif
#ifdef PPI_DEBUG2
GPI_RESOURCE_RESERVE(NRF_PPI_CH, PPI_DEBUG2);
#endif

#define CCR_MAIN_COMPARE         (MAIN_TIMER->CC[CCI_MAIN_COMPARE])
#define CCR_MAIN_START_READY_END (MAIN_TIMER->CC[CCI_MAIN_START_READY_END])
#define CCR_MAIN_ADDRESS         (MAIN_TIMER->CC[CCI_MAIN_ADDRESS])
#define CCR_MAIN_RSSI_START      (MAIN_TIMER->CC[CCI_MAIN_RSSI_START])
#define CCR_MAIN_RSSI            (MAIN_TIMER->CC[CCI_MAIN_RSSI])
//#define CCR_MAIN_PAYLOAD			(MAIN_TIMER->CC[CCI_MAIN_PAYLOAD])

#define INTEN_MAIN_COMPARE BV_BY_NAME_PREEXP(CONCAT(TIMER_INTENSET_COMPARE, CCI_MAIN_COMPARE), Set)

GPI_RESOURCE_RESERVE(NRF_TIMER_CC, MAIN_TIMER_INDEX, CCI_MAIN_COMPARE);
GPI_RESOURCE_RESERVE(NRF_TIMER_CC, MAIN_TIMER_INDEX, CCI_MAIN_START_READY_END);
GPI_RESOURCE_RESERVE(NRF_TIMER_CC, MAIN_TIMER_INDEX, CCI_MAIN_ADDRESS);
GPI_RESOURCE_RESERVE(NRF_TIMER_CC, MAIN_TIMER_INDEX, CCI_MAIN_RSSI_START);
GPI_RESOURCE_RESERVE(NRF_TIMER_CC, MAIN_TIMER_INDEX, CCI_MAIN_RSSI);
//GPI_RESOURCE_RESERVE(NRF_TIMER_CC, MAIN_TIMER_INDEX, CCI_MAIN_PAYLOAD);

#ifdef GPIOTE_DEBUG1
GPI_RESOURCE_RESERVE(NRF_GPIOTE_CH, GPIOTE_DEBUG1);
#endif
#ifdef GPIOTE_DEBUG2
GPI_RESOURCE_RESERVE(NRF_GPIOTE_CH, GPIOTE_DEBUG2);
#endif

//**************************************************************************************************

#ifdef DEBUG_GPIO
  #define LED_ISR(name, led)                                                                       \
      CONCAT(name, _)();                                                                           \
      void name()                                                                                  \
      {                                                                                            \
          gpi_led_toggle(led);                                                                     \
          CONCAT(name, _)();                                                                       \
          gpi_led_toggle(led);                                                                     \
      }                                                                                            \
      void CONCAT(name, _)()
#else
  #define LED_ISR(name, led) void name()
#endif

//**************************************************************************************************
// radio timing constants, in timer ticks (PCLK16M)

#define PPI_DELAY                  1

// nRF spec. states that TASKS_TXEN -> EVENTS_READY = 40...40us (t_TXEN,FAST), while at the same time
// it says that this delay has a typical jitter of 0.25us (t_READYJITTER) [4413_417 v1.2 6.20.15.8 and 6.20.15.10].
// Hence, for the sake of precise timing we avoid using the TXREADY->START shortcut and trigger
// TASKS_START manually RADIO_TX_RAMP_UP_TOLERANCE after the nominal RADIO_TX_RAMP_UP_TIME.
#define RADIO_TX_RAMP_UP_TIME      GPI_TICK_US_TO_FAST(40)
#define RADIO_TX_RAMP_UP_TOLERANCE GPI_TICK_US_TO_FAST(1)

// Rx ramp-up is less time critical than Tx ramp-up because some tolerance is needed anyhow
// (to compensate for clock drift)
#define RADIO_RX_RAMP_UP_TIME      GPI_TICK_US_TO_FAST(40)

// TASKS_START (from TXIDLE state) -> packet on air
// precise value is unknown so far
#define RADIO_TX_START_DELAY       0
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

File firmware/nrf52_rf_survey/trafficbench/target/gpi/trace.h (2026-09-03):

/***************************************************************************************************
 ***************************************************************************************************
 *
 *	Copyright (c) 2018 - 2024, Networked Embedded Systems Lab, TU Dresden
 *	All rights reserved.
 *
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
 *	THIS SOFTWARE IS PROVIDED BY THE COPYRIGHT HOLDERS AND CONTRIBUTORS "AS IS" AND
 *	ANY EXPRESS OR IMPLIED WARRANTIES, INCLUDING, BUT NOT LIMITED TO, THE IMPLIED
 *	WARRANTIES OF MERCHANTABILITY AND FITNESS FOR A PARTICULAR PURPOSE ARE
 *	DISCLAIMED. IN NO EVENT SHALL THE COPYRIGHT HOLDER BE LIABLE FOR ANY
 *	DIRECT, INDIRECT, INCIDENTAL, SPECIAL, EXEMPLARY, OR CONSEQUENTIAL DAMAGES
 *	(INCLUDING, BUT NOT LIMITED TO, PROCUREMENT OF SUBSTITUTE GOODS OR SERVICES;
 *	LOSS OF USE, DATA, OR PROFITS; OR BUSINESS INTERRUPTION) HOWEVER CAUSED AND
 *	ON ANY THEORY OF LIABILITY, WHETHER IN CONTRACT, STRICT LIABILITY, OR TORT
 *	(INCLUDING NEGLIGENCE OR OTHERWISE) ARISING IN ANY WAY OUT OF THE USE OF THIS
 *	SOFTWARE, EVEN IF ADVISED OF THE POSSIBILITY OF SUCH DAMAGE.
 *
 ***********************************************************************************************//**
 *
 *	@file					gpi/trace.h
 *
 *	@brief					Macros for log messages, facilitating a consistent handling w.r.t. the
 *							output channel, format, and (de-)activation of message types / groups.
 *
 * @internal
 *	@version				\$Id: 23d87a7ef22984f50796757d4c7c028ffded82fb $
 *	@noop @date				git log -1 <filename>
 *
 *	@author					Carsten Herrmann
 * @endinternal
 *
 ***************************************************************************************************

 	@details

	TODO
	- GPI_TRACE_MODE erläutern (ggf. Text verschieben)
	- message groups
	- message types
	- platform-specific settings

 **************************************************************************************************/

#ifndef __GPI_TRACE_H__
#define __GPI_TRACE_H__

//**************************************************************************************************
//***** Includes ***********************************************************************************

// internal helper macros for stringification
#define GPI_TRACE_STRINGIFY2(x) #x
#define GPI_TRACE_STRINGIFY(x)  GPI_TRACE_STRINGIFY2(x)

// include project-specific setup file (if defined)
// GPI_TRACE_SETUP_FILE can be used to manage the current project's trace settings at a central
// place. Including it here ensures that all settings (in particular GPI_TRACE_MODE) are valid
// before they get evaluated in preprocessor conditions below.
#ifdef GPI_TRACE_SETUP_FILE
  #include GPI_TRACE_STRINGIFY(GPI_TRACE_SETUP_FILE)
#elif defined(GPI_SETUP_FILE)
  #include GPI_TRACE_STRINGIFY(GPI_SETUP_FILE)
#endif

// check and complete settings
#ifndef GPI_TRACE_MODE
  #define GPI_TRACE_MODE GPI_TRACE_MODE_NO_TRACE
#endif

#include "gpi/platform_spec.h"      // GPI_PLATFORM_PATH()
#include GPI_PLATFORM_PATH(trace.h) // GPI_TRACE_VA_SIZE_MAX
#include "gpi/tools.h"              // VA_NUM, ASSERT_CT, LSB, ...

#include <inttypes.h> // (u)int..._t, PRI...
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

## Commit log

2025-07-01 ⬆ Bump shepherd-core from 2025.5.3 to 2025.6.3
    ---
    updated-dependencies:
    - dependency-name: shepherd-core
    dependency-version: 2025.6.3
    dependency-type: direct:production
    update-type: version-update:semver-minor
    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
2025-07-01 ⬆ Bump xonsh from 0.19.3 to 0.19.9
    - dependency-name: xonsh
    dependency-version: 0.19.9
    update-type: version-update:semver-patch
    ...
    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
2025-07-07 add target programmer
    [Bill of Materials.xlsx, Pick Place.csv, target_adapt_usb_Assembly_Notes.gbr, target_adapt_usb_Bottom_Designator.gbr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]
2026-04-27 Dev (#71)
    * linting
    * update tooling & remove env-lock
    * enable more warnings for nrf-deep-sleep compilation
    * update tooling and doc
    * update target doc
    * Create target_cage_PLA_x16.3mf
    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
    [target_cage_PLA_x16.3mf]
